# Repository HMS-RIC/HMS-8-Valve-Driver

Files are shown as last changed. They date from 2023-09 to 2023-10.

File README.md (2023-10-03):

# HMS 8-Channel Valve Driver

A circuit for driving up to 8 small valves.

The board takes 8 channels of digital inputs (3.3V or 5V) and can drive valves at up to 50V and 500mA. Inputs can be connected via BNC connectors (channels 1–4) or a 0.1" header (all 8 channels). Optional push buttons on channels 1–4 allow for manual valve activation (e.g., to flush or clean the valve lines).

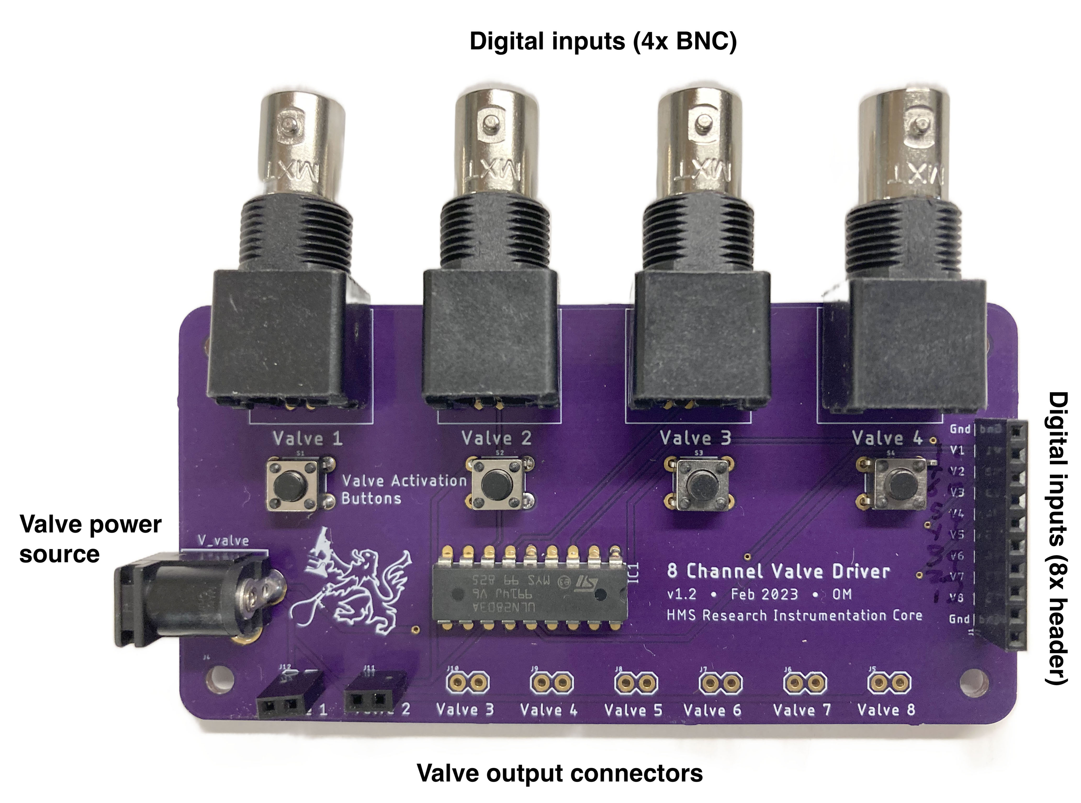
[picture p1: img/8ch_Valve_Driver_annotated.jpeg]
Valve driver circuit board


## Fabrication and Assembly

1) Order a batch of printed circuit boards (PCBs) using the provided Gerber files. 
	- You can upload the [Gerber .zip file](Gerbers/HMS-8-Channel-Valve-Driver-v1.3-Gerbers.zip?raw=true) to a online PCB fabricator, like [OSH Park](https://oshpark.com/) or [DK Red](https://www.digikey.com/en/pcb-builder/?p=dkred) and use the default settings for a 2-layer board.

2) Order the components listed in the Bill of Materials, and solder them into the PCB as shown in the photo above.

**Notes**
- Make sure to place the transistor array chip (ULQ2803A) in the correct orientation (the notch on the chip should line up with the silkscreen).
- Input connectors (BNC or 1x10 header) are optional depending on how you plan to use the board and how many channels you'll need.
- Similarly, manual valve control buttons are optional.

#### Output connectors
You have several choices for the output connectors to the valves since the holes in the board have standard 0.1" spacing. Two options are shown in the images below:
- A simple 0.1" rectangular socket (or header). Some valves can just plug right in (like the Lee LHD series show in the photo).
- A 0.1" screw terminal. Makes it easier to connect directly to wires.
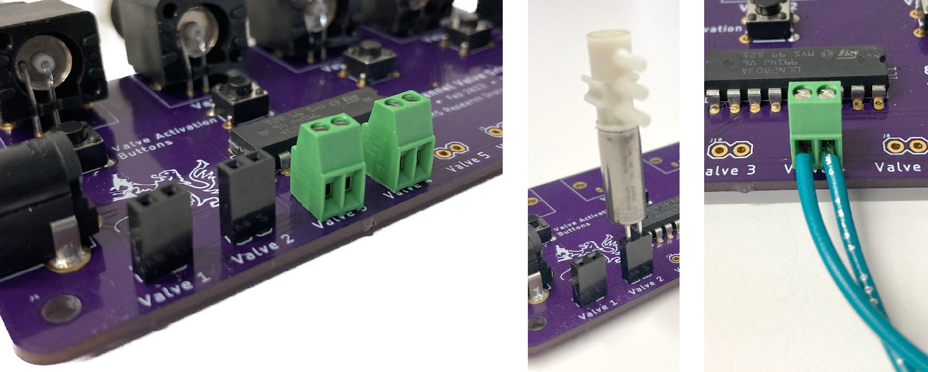
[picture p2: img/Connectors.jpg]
Output connector options


## Usage

1) Plug in a "wall-wart" power supply with the correct voltage for your valves (likely 5V, 12V, or 24V). Make sure the power supply can provide enough current for all the valves you plan to use (or at least as many valves as might be on at once).

2) Connect valves to the output connectors. NOTE: Make sure the valves draw 500mA or less.

3) Provide digital signals to the valve input lines. These may be 3.3V or 5V signals, and might come from a device like an Arduino or a DAQ (data acquisition) board. Make sure that the valve driver and the signal generating device share a common ground connection, either through the BNC shield, or the GND pin on the input header. The circuit will energize the valves in response to a HIGH (3–5V) input signal.

4) If needed, you can also use the buttons to manually energize the valves.

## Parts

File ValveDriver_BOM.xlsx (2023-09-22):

Ref | Value | Device | Digikey part | Unit Price (@qty=10) | Notes
IC1 |  | ULN2803A | 497-2356-5-ND | $2.80 | Can also use ULQ2803A (497-2362-5-ND)
J1 |  | 0.1" Header 1X10" | S7043-ND | $0.68
J4 |  | POWER_JACK | CP-202A-ND | $0.70
J5–12 |  | Valve connector (option A) | S7035-ND | $0.33 | Socket
 |  | Valve connector (option B) | A98333-ND | $1.40 | Screw Terminal
J15–18 |  | BNC connector | WM5514-ND | $2.50
S1–4 |  | 6mm tactile switch | 1528-367-ND |  | (Bag of 20x)
 |  | NOTE: All components besides the driver chip (IC1) are commodity parts and can be swapped with suitable alternatives

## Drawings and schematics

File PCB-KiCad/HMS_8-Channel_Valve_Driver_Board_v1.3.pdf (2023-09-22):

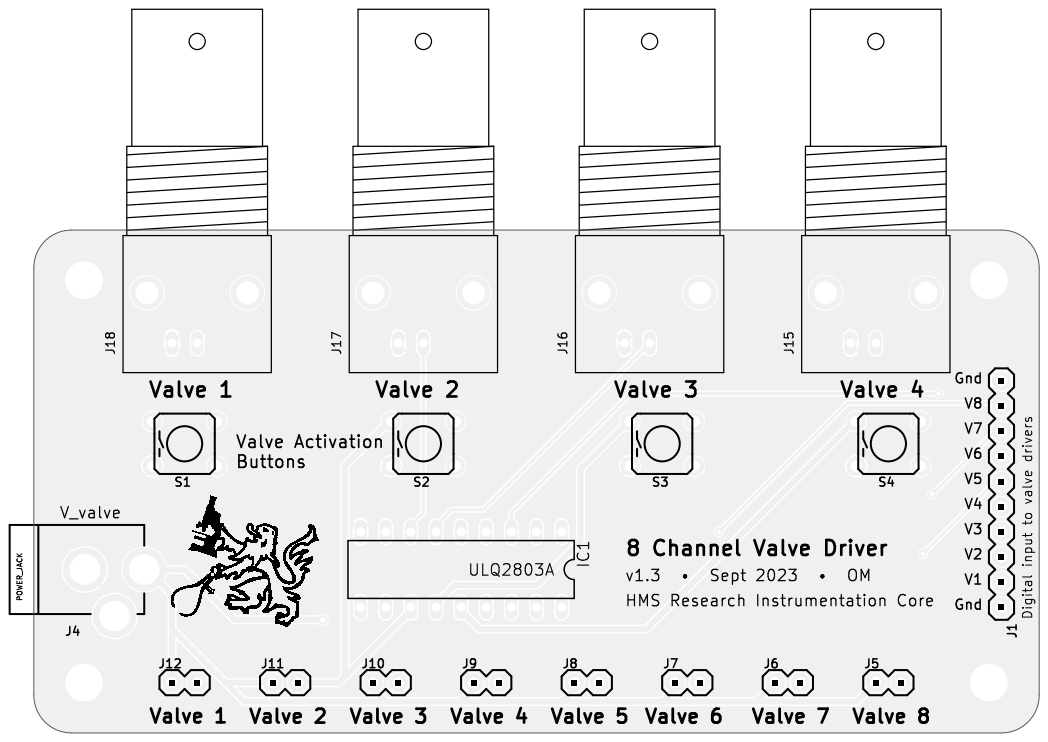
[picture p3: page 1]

Id: 1/1 Title: File: HMS_8ValveDriver.kicad_pcb Sheet: POWER_JACK

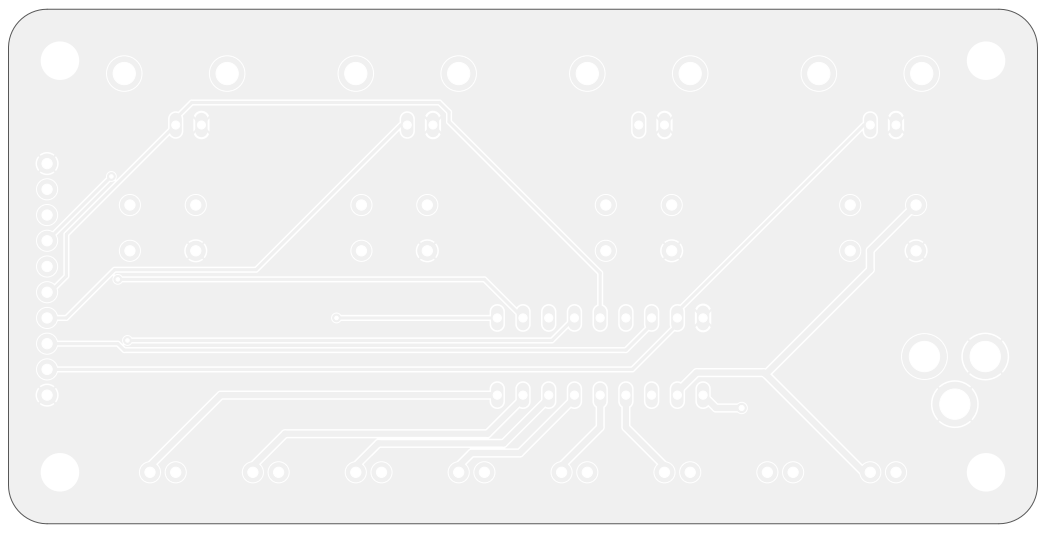
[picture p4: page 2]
D Date: KiCad; pcbnew 7.0.7 Size: A4; Rev:

Id: 1/1 Title: File: HMS_8ValveDriver.kicad_pcb Sheet:

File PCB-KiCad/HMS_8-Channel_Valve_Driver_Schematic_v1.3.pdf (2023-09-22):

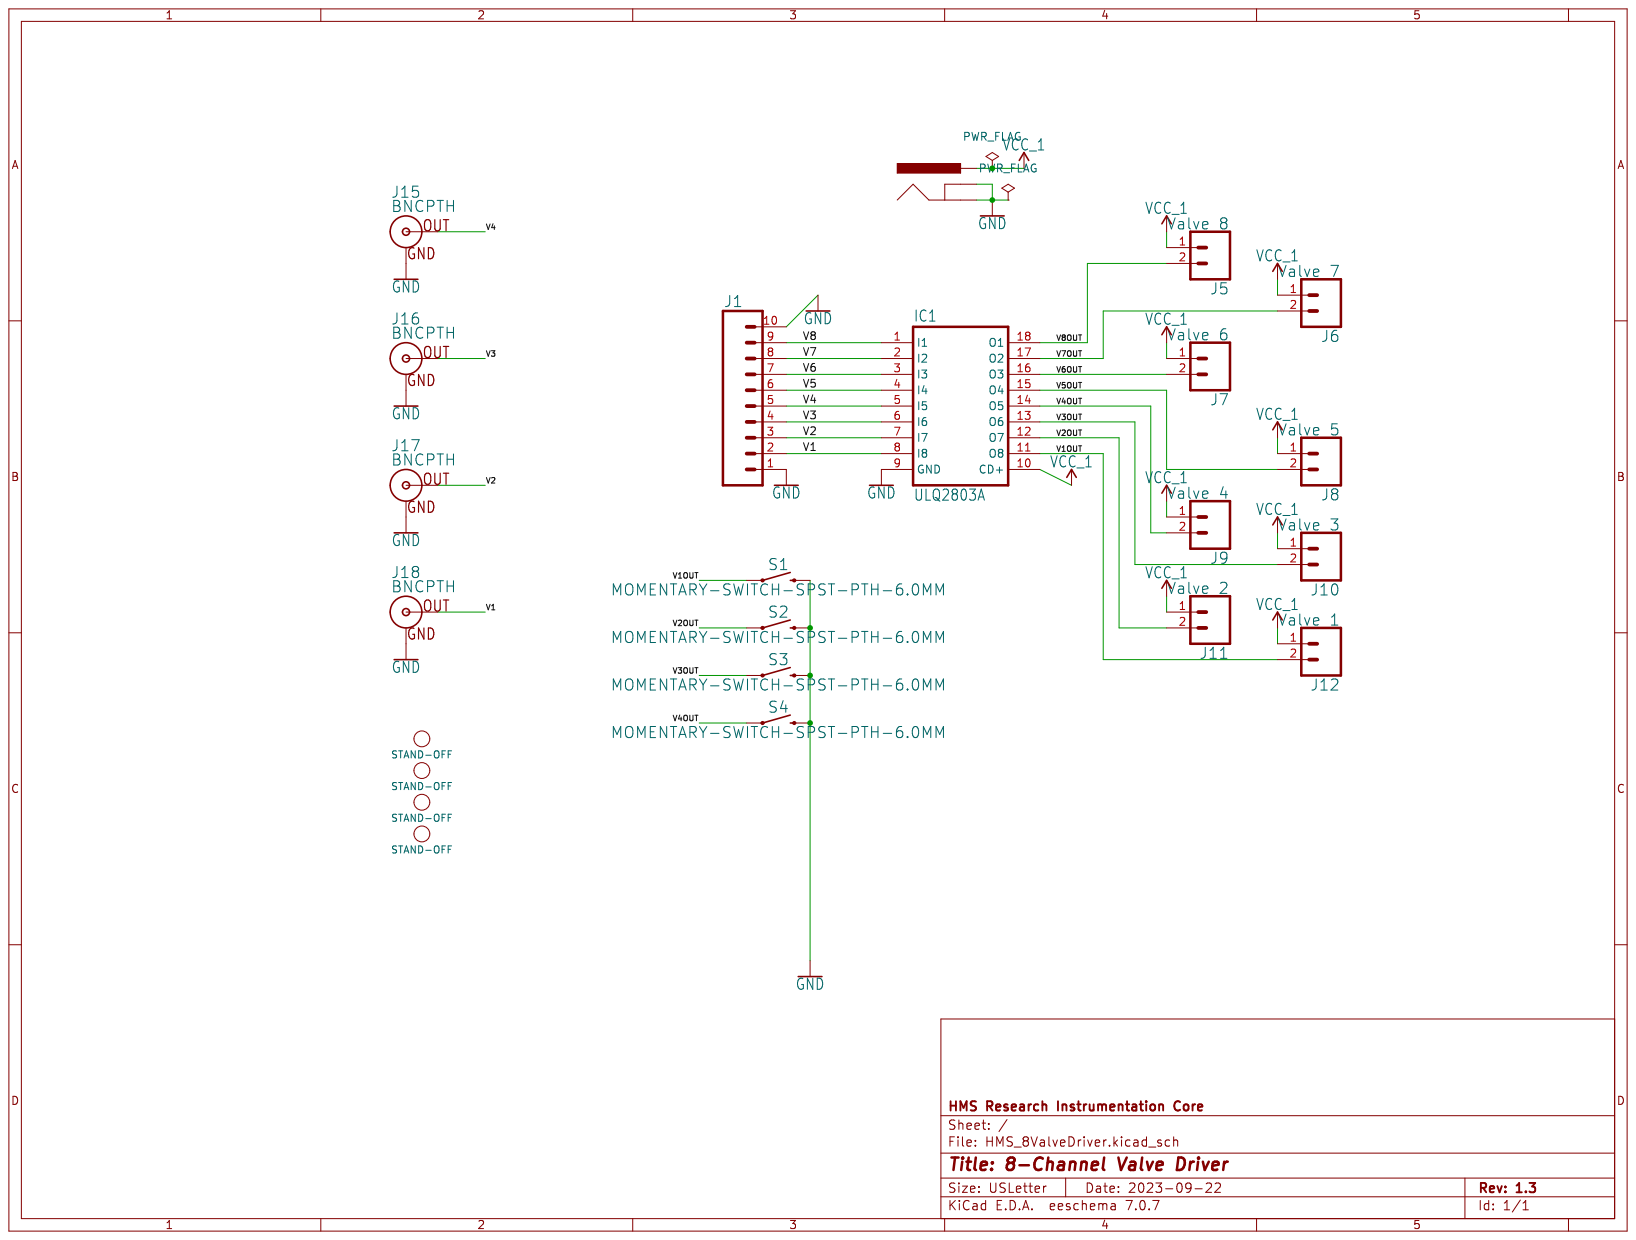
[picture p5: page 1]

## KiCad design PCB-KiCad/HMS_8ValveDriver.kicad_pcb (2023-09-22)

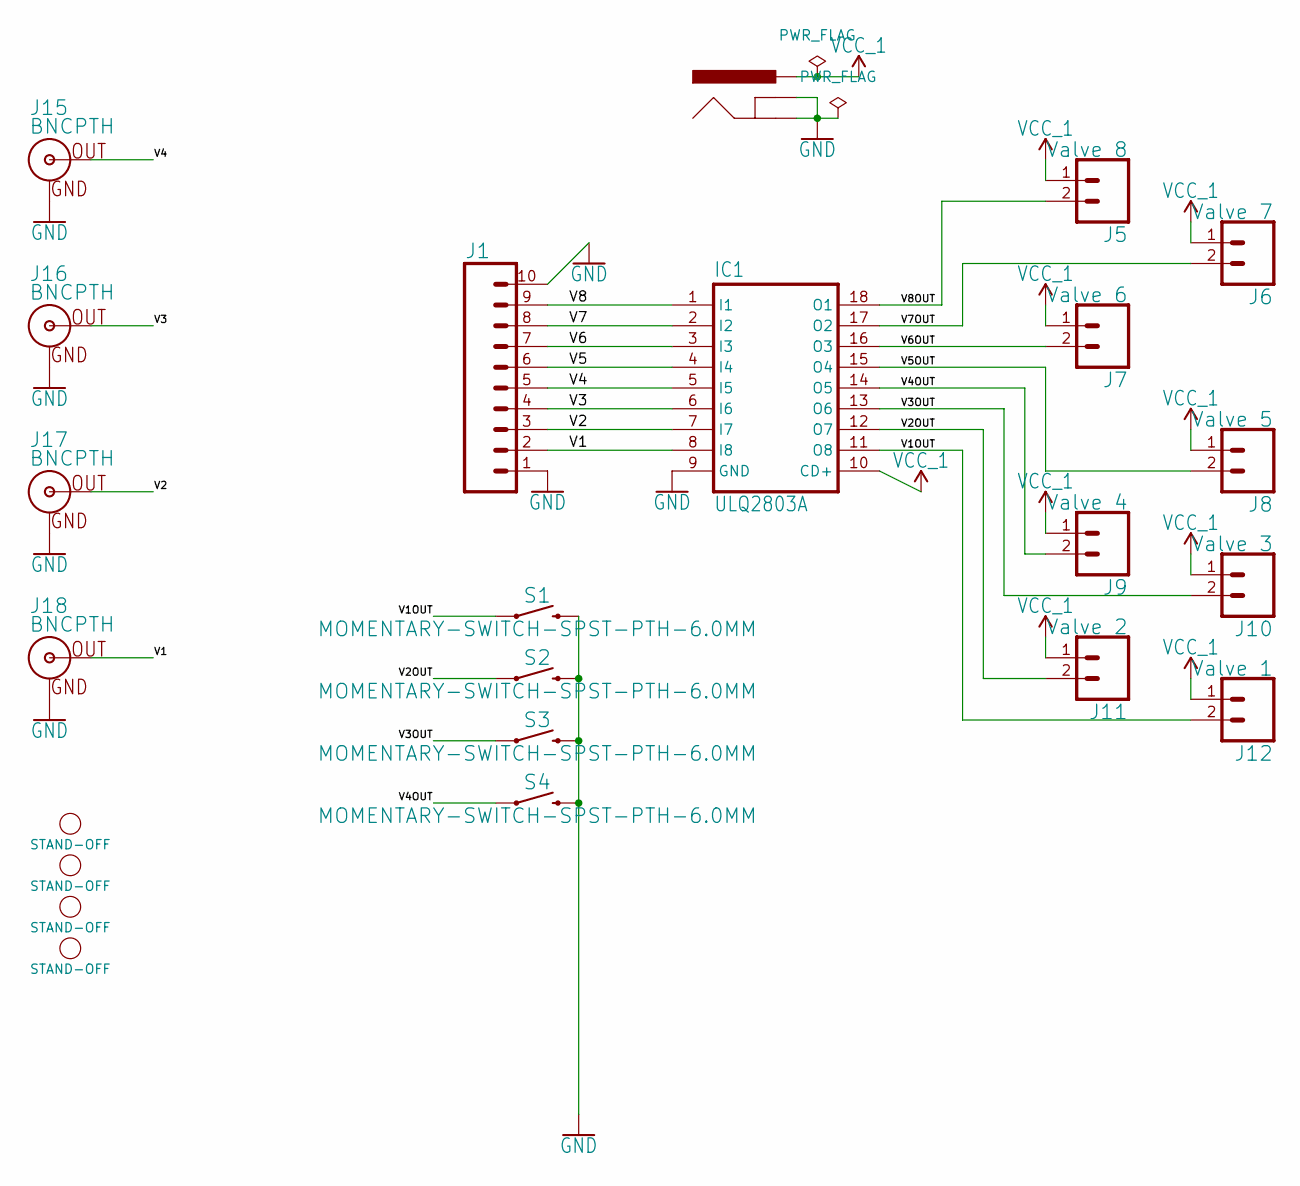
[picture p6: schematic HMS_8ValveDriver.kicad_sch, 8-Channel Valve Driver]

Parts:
H1, H2, H3, H4: STAND-OFF
IC1: ULQ2803A; DIL18
J1: CONN_10"; 1X10
J4: POWER_JACK; POWER_JACK_PTH
J5: Valve 8; 1X02
J6: Valve 7; 1X02
J7: Valve 6; 1X02
J8: Valve 5; 1X02
J9: Valve 4; 1X02
J10: Valve 3; 1X02
J11: Valve 2; 1X02
J12: Valve 1; 1X02
J15, J16, J17, J18: BNCPTH; BNC
S1, S2, S3, S4: MOMENTARY-SWITCH-SPST-PTH-6.0MM; TACTILE_SWITCH_PTH_6.0MM

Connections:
/V1: IC1.8 (I8), J1.2, J18.S (OUT)
/V1OUT: IC1.11 (O8), J12.2, S1.1
/V2: IC1.7 (I7), J1.3, J17.S (OUT)
/V2OUT: IC1.12 (O7), J11.2, S2.1
/V3: IC1.6 (I6), J1.4, J16.S (OUT)
/V3OUT: IC1.13 (O6), J10.2, S3.1
/V4: IC1.5 (I5), J1.5, J15.S (OUT)
/V4OUT: IC1.14 (O5), J9.2, S4.1
/V5: IC1.4 (I4), J1.6
/V5OUT: IC1.15 (O4), J8.2
/V6: IC1.3 (I3), J1.7
/V6OUT: IC1.16 (O3), J7.2
/V7: IC1.2 (I2), J1.8
/V7OUT: IC1.17 (O2), J6.2
/V8: IC1.1 (I1), J1.9
/V8OUT: IC1.18 (O1), J5.2
GND: IC1.9 (GND), J1.1, J1.10, J4.GND, J4.GNDBREAK, J15.GND, J16.GND, J17.GND, J18.GND, S1.3 (2), S2.3 (2), S3.3 (2), S4.3 (2)
VCC_1: IC1.10 (CD+), J4.PWR, J5.1, J6.1, J7.1, J8.1, J9.1, J10.1, J11.1, J12.1

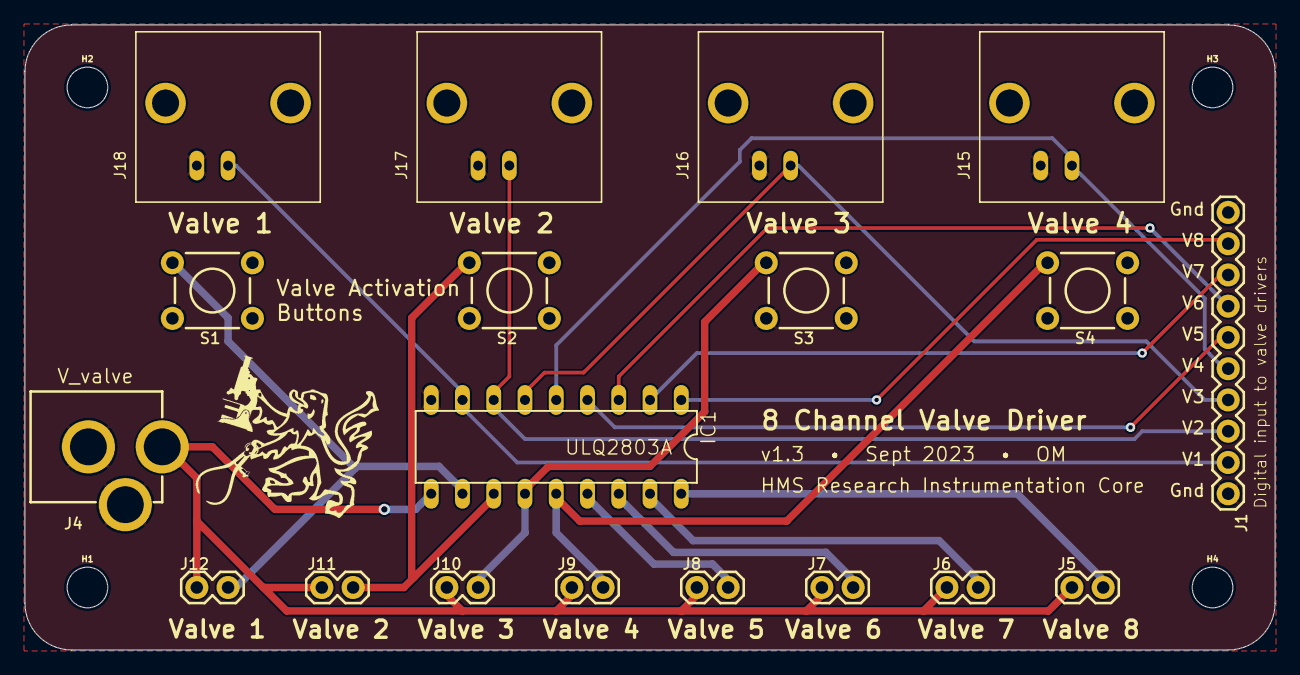
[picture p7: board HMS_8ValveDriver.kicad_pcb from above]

Board: 2 copper layers, 101.6 x 50.8 mm, 24 parts (0 on the bottom side), 18 nets.

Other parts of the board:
U$7: RIC_LOGO_BIG

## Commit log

2023-09-22 Update BOM; Generate Gerbers
    [HMS_8ValveDriver-B_Cu.gbr, HMS_8ValveDriver-B_Mask.gbr, HMS_8ValveDriver-B_Paste.gbr, HMS_8ValveDriver-B_Silkscreen.gbr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]
2023-10-03 Remove Eagle files
    [HMS_8ValveDriver.brd, HMS_8ValveDriver.sch]
